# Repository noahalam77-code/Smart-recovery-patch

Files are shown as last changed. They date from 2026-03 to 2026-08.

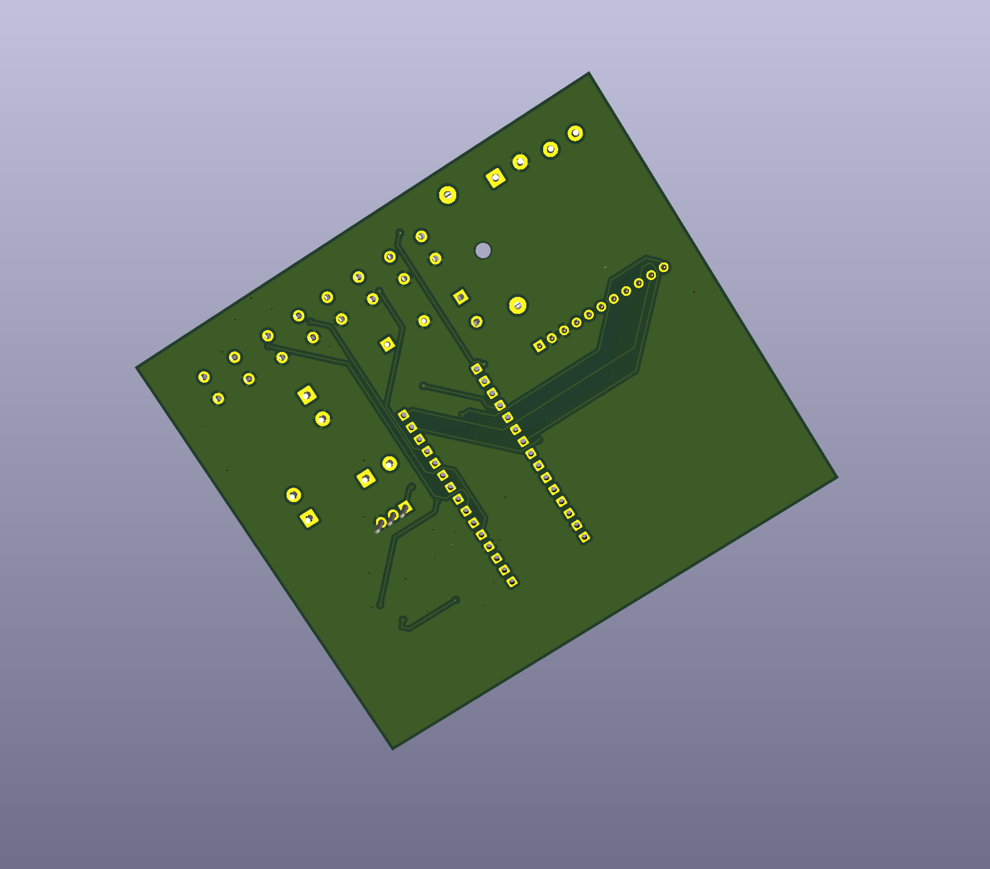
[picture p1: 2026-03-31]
pcb/Pcb3dBttm.png

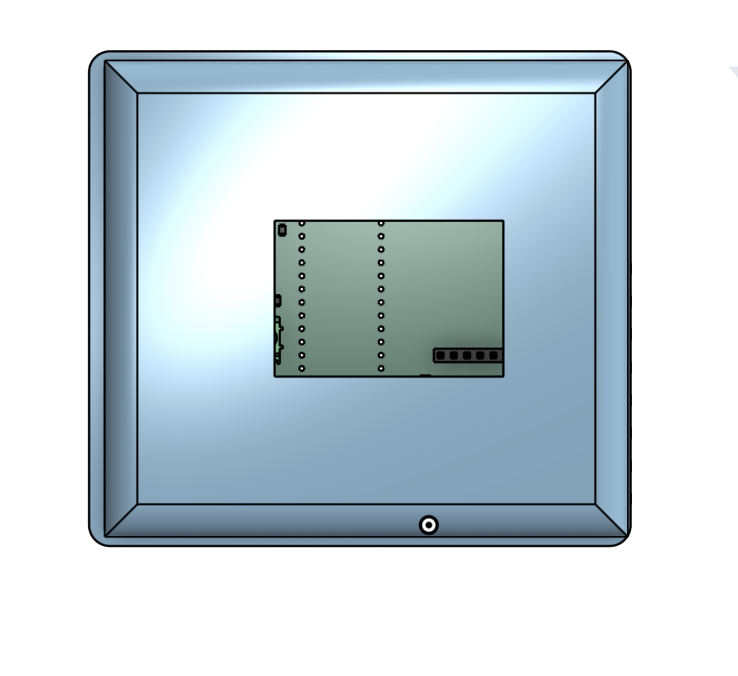
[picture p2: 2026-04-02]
CAD/CaseTop.png

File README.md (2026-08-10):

# TheraPatch

## Repository file structure
- BOM: JCLPCB BOM & regular BOM
- CADfiles: STEP files, STL files, and assembly notes
- PCB: PCB files, Gerber files, schematic images, and PCB images
- Firmware: Code & flashing instructions

## What it is
TheraPatch is a handheld therapeutic device designed to help mitigate the effects of injuries such as bruises, sprains, minor cuts, and more. By using a reverse-polarity system via an H-bridge, TheraPatch can heat the affected area (dilating blood vessels) or cool it (constricting blood vessels), both of which have been shown to help with injury healing at certain temperatures (which TheraPatch can achieve). 

## Motivation
I created TheraPatch with the primary motivation of helping people with common sports/activty related injuries while maintaining an efficient device to do so. Most of the time, when you have a bruise or scrape, you'd rely on disposable ice packs or inefficient heating pads, which are wasteful and time-consuming for long-term use. TheraPatch offers an effective, infinitely reusable solution to this. Instead of freezing water for 3-4 hours or boiling a heatpack everytime you need to reuse it, all you do with TheraPatch is plug and play. It's effective for athletes and normal people.

## Use of TheraPatch
To use the TheraPatch, first ensure your battery/wall adapter is plugged in. Then locate the 4 buttons on the top of the device; these buttons will allow you to set your desired parameters by moving through the menus: mode (hot/cold), set temp, and set time. After your desired settings are set, click the start button to initiate your therapy session, and place the side with the Peltier facing out against the affected area

## How it works
The TheraPatch looks like a simple black-and-white hot-cold block, but its guts are far more advanced. In electronics, generating heat is relatively simple. Electrons bump into each other rapidly in the wire, vibrating and thus creating the heat we feel. This is the easy part; cooling is the real engineering challenge. To cool it, I used a Peltier module, which transfers heat from one side to the other. Now, this needs to be driven by a heatsink and a fan to effectively cool. To achieve heating and cooling on the same side, I used an H bridge. The H-bridge module reverses the polarity in a Peltier module, meaning that when one side is positive and the other is negative, it cools; vice versa. All of this is controlled by a custom 4-layer PCB I designed in KiCad, with an ATmega328P as my microcontroller. The firmware reads a thermistor pressed against the Peltier plate and uses a bang-bang controller to turn the Peltier on/off to reach the desired temperature. This is all run by a rechargeable 12V battery, which charges via USB-C or a 12V wall adapter. These components are combined in a logical order in a CAD-designed box with a hole for all the input plugs and vent fans for air circulation.

Here are images of my project

## CAD imgaes:

Screenshot 2026-08-10 at 1 19 23 PM

Screenshot 2026-08-10 at 1 16 25 PM

Screenshot 2026-08-10 at 1 16 42 PM

Screenshot 2026-08-10 at 1 17 00 PM

Screenshot 2026-08-10 at 1 17 14 PM

Screenshot 2026-08-10 at 1 17 29 PM

Screenshot 2026-08-10 at 1 17 42 PM

Screenshot 2026-08-10 at 1 17 55 PM

## Link to Onshape case:

https://cad.onshape.com/documents/d627d659f05dae60588ec801/w/ad74ef98cd2d7a13cb59f9ec/e/f50ed022a94792dc2cfe6130?renderMode=0&uiState=6a4947abb17d022f5d41873a

# PCB (Signal Layer and ground):

## F.cu (signal traces and ground):

Screenshot 2026-06-03 at 1 51 27 AM

## In1.cu(ground):

Screenshot 2026-06-03 at 1 52 55 AM

## In2.cu (5V & 12V power)

Screenshot 2026-06-03 at 1 53 45 AM

## B.cu (signal traces and ground):

Screenshot 2026-06-03 at 1 54 23 AM

## 3D:

Screenshot 2026-06-03 at 1 55 00 AM

# Schematic (wiring diagram):

## Pic_1:

Screenshot 2026-06-03 at 1 55 57 AM

## Pwr:

Screenshot 2026-06-03 at 1 56 46 AM

## BOM(main)

| Item | Quantity | Unit price | Total price | Descrption | Link |
|------|----------|-----------|-------------|------------|------|
| Fan | 1 | 4.81 | 4.81 | Facliate heaitng & cooling | [Link](https://www.aliexpress.us/item/3256808462428286.html?spm=a2g0o.productlist.main.1.6babkeHNkeHNko&algo_pvid=c39052da-f6dd-4b67-816a-d90e786c586d&algo_exp_id=c39052da-f6dd-4b67-816a-d90e786c586d-0&pdp_ext_f=%7B%22order%22%3A%2262%22%2C%22eval%22%3A%221%22%2C%22fromPage%22%3A%22search%22%7D&pdp_npi=6%40dis%21USD%2111.50%214.79%21%21%2178.10%2132.53%21%402101d6ff17774285328603962e8757%2112000046088904920%21sea%21US%210%21ABX%211%210%21n_tag%3A-29910%3Bd%3Ad6b644bf%3Bm03_new_user%3A-29895%3BpisId%3A5000000204886261&curPageLogUid=VweLjIS1lGkI&utparam-url=scene%3Asearch%7Cquery_from%3A%7Cx_object_id%3A1005008648743038%7C_p_origin_prod%3A) |
| Peltier | 1 | 3.90$ | $3.90 | Cool and heat | [Link](https://www.aliexpress.us/item/3256806863842277.html?src=google&gatewayAdapt=glo2usa) |
| Heatsink | 2 | 4.80$ | $9.79 | Disspate heat | [Link](https://www.amazon.com/Awxlumv-Aluminum-60mmx60mmx15mm-Conductive-Amplifier/dp/B0DNLXD4NL) |
| LCD screen | 1 | 0.9900$ | 0.9900$ | Displaying modes | [Link](https://www.aliexpress.us/item/3256807264700302.html?spm=a2g0o.productlist.main.15.3bb1HGrhHGrhWv&algo_pvid=f071bd73-714c-4717-acaa-3f74ef8deb17&algo_exp_id=f071bd73-714c-4717-acaa-3f74ef8deb17-14&pdp_ext_f=%7B%22order%22%3A%223710%22%2C%22eval%22%3A%221%22%2C%22fromPage%22%3A%22search%22%7D&pdp_npi=6%40dis%21USD%213.14%210.99%21%21%213.14%210.99%21%4021030a6217776832914577048eb84d%2112000040806152744%21sea%21US%210%21ABX%211%210%21n_tag%3A-29910%3Bd%3Ad6b644bf%3Bm03_new_user%3A-29895%3BpisId%3A5000000203537378&curPageLogUid=GNgXD2HWAIP5&utparam-url=scene%3Asearch%7Cquery_from%3A%7Cx_object_id%3A1005007451015054%7C_p_origin_prod%3A#nav-specification) |
| Thermistor | 1 | 0.9500$ | 0.9500$ | Temp meauring | [Link](https://www.adafruit.com/product/4890?srsltid=AfmBOopGi_4mLQSeRw3V9sBgnchAdNrL2zdLeJHItTaAc1rCL6Ne9o2P) |
| Battery | 1 | 26.99$ | $26.99 | Used as main source of power (for moblity) BMS confirmed | [Link](https://liionwholesale.com/products/3s1p-3-7v-3500mah-18650-battery-with-wires-and-connector-lg-mj1-cell-inside?srsltid=AfmBOopbHVjk3o8ywzVI_wQWHKZhMZp1uCq0ynXZWNxGTDKPMvd9ZKI6&variant=31229057794117) |
| Wire | 1 | 2.2300$ | 2.23$ | Battery caddy, peliter and fan extesion | [Link](https://www.aliexpress.us/item/3256802140205012.html?spm=a2g0o.productlist.main.8.4437dfNPdfNPLw&aem_p4p_detail=202606281750527933413825797320002756170&algo_pvid=c53e4217-68c6-4b26-9b29-3624128716f9&algo_exp_id=c53e4217-68c6-4b26-9b29-3624128716f9-7&pdp_ext_f=%7B%22order%22%3A%22123%22%2C%22eval%22%3A%221%22%2C%22fromPage%22%3A%22search%22%7D&pdp_npi=6%40dis%21USD%214.70%212.79%21%21%214.70%212.79%21%402103212b17826942522901169e02c1%2112000052586672765%21sea%21US%210%21ABX%211%210%21n_tag%3A-29910%3Bd%3Ad6b644bf%3Bm03_new_user%3A-29895%3BpisId%3A5000000208023469&curPageLogUid=CY0b8Pvel5HR&utparam-url=scene%3Asearch%7Cquery_from%3A%7Cx_object_id%3A1005002326519764%7C_p_origin_prod%3A&search_p4p_id=202606281750527933413825797320002756170_2) |
| Wall adapter | 1 | $1.28 | $1.28 | 2nd way of recving power (1st battery) | [Link](https://www.aliexpress.us/item/3256806555593510.html?spm=a2g0o.productlist.main.5.103eNCpVNCpVMj&algo_pvid=3d352d1e-bc43-4e77-9d29-16e4344ed46b&algo_exp_id=3d352d1e-bc43-4e77-9d29-16e4344ed46b-4&pdp_ext_f=%7B%22order%22%3A%221992%22%2C%22eval%22%3A%221%22%2C%22fromPage%22%3A%22search%22%7D&pdp_npi=6%40dis%21USD%2111.78%211.28%21%21%2179.73%218.69%21%402101eecd17826947715547891e5012%2112000038157481542%21sea%21US%210%21ABX%211%210%21n_tag%3A-29910%3Bd%3Ad6b644bf%3Bm03_new_user%3A-29895%3BpisId%3A5000000209510139&curPageLogUid=H50idJ0yOZub&utparam-url=scene%3Asearch%7Cquery_from%3A%7Cx_object_id%3A1005006741908262%7C_p_origin_prod%3A) |
| M2 screw 8mm | 100 | 0.0100$ | $1.35 | screws for battery caddy | [Link](https://www.aliexpress.us/item/2251832857570651.html?spm=a2g0o.productlist.main.3.4e3cdUVEdUVEfl&algo_pvid=ea8d64ad-4af7-4109-af97-4e674e97f9e5&algo_exp_id=ea8d64ad-4af7-4109-af97-4e674e97f9e5-2&pdp_ext_f=%7B%22order%22%3A%2216288%22%2C%22eval%22%3A%221%22%2C%22fromPage%22%3A%22search%22%7D&pdp_npi=6%40dis%21USD%211.35%210.99%21%21%211.35%210.99%21%402103129f17825915196483426e5a8e%2112000020018123413%21sea%21US%210%21ABX%211%210%21n_tag%3A-29910%3Bd%3Ad6b644bf%3Bm03_new_user%3A-29895%3BpisId%3A5000000208023469&curPageLogUid=WMcjfyJWRpdQ&utparam-url=scene%3Asearch%7Cquery_from%3A%7Cx_object_id%3A33043885403%7C_p_origin_prod%3A) |
| M2 screw 14mm | 100 | 0.0100$ | $1.35 | screws for main case | [Link](https://www.aliexpress.us/item/2251832857570651.html?spm=a2g0o.productlist.main.3.4e3cdUVEdUVEfl&algo_pvid=ea8d64ad-4af7-4109-af97-4e674e97f9e5&algo_exp_id=ea8d64ad-4af7-4109-af97-4e674e97f9e5-2&pdp_ext_f=%7B%22order%22%3A%2216288%22%2C%22eval%22%3A%221%22%2C%22fromPage%22%3A%22search%22%7D&pdp_npi=6%40dis%21USD%211.35%210.99%21%21%211.35%210.99%21%402103129f17825915196483426e5a8e%2112000020018123413%21sea%21US%210%21ABX%211%210%21n_tag%3A-29910%3Bd%3Ad6b644bf%3Bm03_new_user%3A-29895%3BpisId%3A5000000208023469&curPageLogUid=WMcjfyJWRpdQ&utparam-url=scene%3Asearch%7Cquery_from%3A%7Cx_object_id%3A33043885403%7C_p_origin_prod%3A) |
| Dupont connectors | 40 | 0.0253$ | 1.01$ | connectors for LCD and ISP proggarmer | [Link](https://www.aliexpress.us/item/3256809185840584.html?spm=a2g0o.productlist.main.4.7725T11aT11aC1&aem_p4p_detail=202606272107031134387990076280002008158&algo_pvid=84f900fb-1f7e-4029-80e1-2e2e9eab2415&algo_exp_id=84f900fb-1f7e-4029-80e1-2e2e9eab2415-3&pdp_ext_f=%7B%22order%22%3A%22686%22%2C%22eval%22%3A%221%22%2C%22fromPage%22%3A%22search%22%7D&pdp_npi=6%40dis%21USD%211.56%211.01%21%21%2110.57%216.87%21%402101e80317826196231237198ed5a5%2112000048899602396%21sea%21US%210%21ABX%211%210%21n_tag%3A-29910%3Bd%3Ad6b644bf%3Bm03_new_user%3A-29895%3BpisId%3A5000000208023469&curPageLogUid=48BAjk6LrSZa&utparam-url=scene%3Asearch%7Cquery_from%3A%7Cx_object_id%3A1005009372155336%7C_p_origin_prod%3A&search_p4p_id=202606272107031134387990076280002008158_2) |
| ISP porgrammer | 1 | 1.9100$ | $1.91 | Flashes code onto the ATMega chip | [Link](https://www.aliexpress.us/item/3256810618247711.html?spm=a2g0o.productlist.main.2.71a9WonxWonxOW&algo_pvid=013dc172-5dcd-4517-a7dc-e44b31c61f77&algo_exp_id=013dc172-5dcd-4517-a7dc-e44b31c61f77-1&pdp_ext_f=%7B%22order%22%3A%2220%22%2C%22eval%22%3A%221%22%2C%22fromPage%22%3A%22search%22%7D&pdp_npi=6%40dis%21USD%212.41%211.91%21%21%212.41%211.91%21%402101d6ff17826055513113304ea732%2112000053555380165%21sea%21US%210%21ABX%211%210%21n_tag%3A-29910%3Bd%3Ad6b644bf%3Bm03_new_user%3A-29895%3BpisId%3A5000000208023469&curPageLogUid=atD9pSQGrkCO&utparam-url=scene%3Asearch%7Cquery_from%3A%7Cx_object_id%3A1005010804562463%7C_p_origin_prod%3A) |
| Buttons | 20 | 0.1095$ | 2.19$ | Switching between menus & 0start/stop | [Link](https://www.aliexpress.us/item/3256801638385730.html?spm=a2g0o.productlist.main.18.6eae9KoY9KoY39&algo_pvid=a04722e0-ab76-4104-b323-04a47393d95b&algo_exp_id=a04722e0-ab76-4104-b323-04a47393d95b-17&pdp_ext_f=%7B%22order%22%3A%2239%22%2C%22eval%22%3A%221%22%2C%22fromPage%22%3A%22search%22%7D&pdp_npi=6%40dis%21USD%213.15%212.59%21%21%213.15%212.59%21%402101eee917825893617621165ec559%2112000017947649837%21sea%21US%210%21ABX%211%210%21n_tag%3A-29910%3Bd%3Ad6b644bf%3Bm03_new_user%3A-29895%3BpisId%3A5000000208023469&curPageLogUid=ypVEuRkxBtEG&utparam-url=scene%3Asearch%7Cquery_from%3A%7Cx_object_id%3A1005001824700482%7C_p_origin_prod%3A) |
| Terminal Block | 5 | 0.0864$ | 0.4300$ | For conencting things without JST conenctor | [Link](https://www.lcsc.com/product-detail/C394556.html?s_z=n_JILN%2520JL126-50002G01) |
| Barrel Jack | 5 | 0.1462$ | $0.73 | Wall power input | [Link](https://www.lcsc.com/product-detail/C720558.html?s_z=n_q_barrel%2520jack%25205A&spm=wm.fly.bg.0.xh&lcsc_vid=QFJaAQFeTlFdU1xXTwILAlBQQQILVwYAQQALAlYEFFYxVlNRTlVfU1NRRlVfXzsOAxUeFF5JWBYZEEoKFBINSQcJGk4NBhADEA4cHktRRVBADxALGw%3D%3D) |
| JST female | 20 | 0.0403$ | 0.81$ | Battery inpt | [Link](https://www.lcsc.com/product-detail/C158012.html?s_z=n_q_C158012&globalKeyword=C158012) |
| 4 Pin connector for LCD | 10 | 0.0807$ | 0.81$ | LCD input | [Link](https://www.lcsc.com/product-detail/C50950.html?s_z=n_q_C50950&globalKeyword=C50950) |
| Arundio flash input | 5 | 0.2238$ | 1.12$ | Pins to flash code | [Link](https://www.lcsc.com/product-detail/C50980.html?s_z=n_q_C50980&globalKeyword=C50980) |
| USB-C | 5 | $0.1857 | $0.93 | Charging | [Link](https://www.lcsc.com/product-detail/C165948.html?s_z=n_q_C165948&globalKeyword=C165948) |
| 5A fuse | 10 | 0.0506$ | $0.51 | PCB | [Link](https://www.lcsc.com/product-detail/C41367229.html?s_z=n_q_t_5A%2520smd%2520fuse&spm=wm.fly.bg.0.xh___wm.ssy.tc.1.tz&lcsc_vid=QFJaAQFeTlFdU1xXTwILAlBQQQILVwYAQQALAlYEFFYxVlNRX1JWRFhbVTsOAxUeFF5JWBYZEEoKFBINSQcJGk4eFQsCAgIaSgADAwAHC0slQ1hcUV1ST1ZADxALGw%3D%3D) |
| 16 Mhz cyrstal | 5 | 0.2372$ | $1.19 | PCB | [Link](https://www.lcsc.com/product-detail/C122519.html?s_z=n_q_C122519&globalKeyword=C122519) |
| Ferrite Bead | 10 | 0.0262$ | $0.26 | PCB | [Link](https://www.lcsc.com/product-detail/C21519.html?s_z=n_q_600%2520ohm%2520ferrite%2520bead%25200805&spm=wm.fly.bg.0.xh&lcsc_vid=QFJaAQFeTlFdU1xXTwILAlBQQQILVwYAQQALAlYEFFYxVlNRTlNeUFZWRFZaXjsOAxUeFF5JWBYZEEoKFBINSQcJGk4eFQsCAgIaSgADAwAHC0slQFFbUVZIHxUDCw%3D%3D) |
| AO3400A | 5 | 0.0846$ | $0.42 | diode for the fan | [Link](https://www.lcsc.com/product-detail/C20917.html?s_z=n_q_C20917&globalKeyword=C20917) |
| SS54 Diode | 10 | 0.0366$ | 0.3700$ | Diode used in buck and input pwr | [Link](https://www.lcsc.com/product-detail/C22452.html?s_z=n_q_SS54%2520diode&spm=wm.fly.bg.0.xh&lcsc_vid=QFJaAQFeTlFdU1xXTwILAlBQQQILVwYAQQALAlYEFFYxVlNRTlNaVVRURldfUzsOAxUeFF5JWBYZEEoKFBINSQcJGk4eFQsCAgIaSgADAwAHC0slT1dZUUoOAwwC) |
| 33uH buck Inductor | 5 | 0.2204$ | 1.10$ | PCB | [Link](https://www.lcsc.com/product-detail/C9400.html?s_z=n_q_t_33uH%2520SMD%2520ind&spm=wm.fly.bg.0.xh___wm.ssy.tc.0.tz&lcsc_vid=QFJaAQFeTlFdU1xXTwILAlBQQQILVwYAQQALAlYEFFYxVlNRT1leX1JUQFNXUTsOAxUeFF5JWBYZEEoKFBINSQcJGk4dAgUUFAk%3D) |
| 2.2uH boost Inductor | 5 | 0.1161$ | $0.58 | PCB | [Link](https://www.lcsc.com/product-detail/C7461347.html?s_z=n_q_CXP0530-2R2M-AG&spm=wm.fly.bg.0.xh&lcsc_vid=QFJaAQFeTlFdU1xXTwILAlBQQQILVwYAQQALAlYEFFYxVlNRT1leX11TRlhaUjsOAxUeFF5JWBYZEEoKFBINSQcJGk4NBhADEA4cHktXRllfSQwSGg0%3D) |
| 120K resistor | 100 | $0.0022 | $0.22 | PCB | [Link](https://www.lcsc.com/product-detail/C2907223.html?s_z=n_q_C2907223&globalKeyword=C2907223) |
| 90K resitor | 10 | $0.0654 | $0.65 | PCB | [Link](https://www.lcsc.com/product-detail/C5123603.html?s_z=n_q_C5123603&globalKeyword=C5123603) |
| 68K resistor | 100 | $0.0021 | $0.21 | PCB | [Link](https://www.lcsc.com/product-detail/C2907283.html?s_z=n_q_C2907283&globalKeyword=C2907283) |
| 51k resistor | 100 | $0.0021 | $0.21 | PCB | [Link](https://www.lcsc.com/product-detail/C2933461.html?s_z=n_q_C2933461&globalKeyword=C2933461) |
| 47K resistor | 100 | $0.0021 | $0.21 | PCB | [Link](https://www.lcsc.com/product-detail/C2930202.html?s_z=n_q_C2930202&globalKeyword=C2930202) |
| 10K resistor | 100 | $0.0020 | $0.20 | PCB | [Link](https://www.lcsc.com/product-detail/C2907219.html?s_z=n_q_C2907219&globalKeyword=C2907219) |
| 5.1K resistor | 100 | $0.00 | $0.27 | PCB | [Link](https://www.lcsc.com/product-detail/C27834.html?s_z=n_q_C27834&globalKeyword=C27834) |
| 3.3K resistor | 100 | $0.0020 | $0.20 | PCB | [Link](https://www.lcsc.com/product-detail/C2907023.html?s_z=n_q_t_3.3K%2520resistor&spm=wm.fly.bg.1.xh___wm.ssy.tc.0.tz&lcsc_vid=QFJaAQFeTlFdU1xXTwILAlBQQQILVwYAQQALAlYEFFYxVlNRT1lfUVBUTlNfXzsOAxUeFF5JWBYZEEoKFBINSQcJGk4eFQsCAgIaSgADAwAHC0slRVZWVFBIHxUDCw%3D%3D) |
| 1k resistor | 100 | $0.0076 | $0.76 | PCB | [Link](https://www.lcsc.com/product-detail/C2907002.html?s_z=n_q_t_0603%25201k%25CE%25A9%2520&spm=wm.fly.bg.0.xh___wm.ssy.tc.0.tz&lcsc_vid=QFJaAQFeTlFdU1xXTwILAlBQQQILVwYAQQALAlYEFFYxVlNeRFBXUFRQT1NcUzsOAxUeFF5JWBYZEEoKFBINSQcJGk4NBhADEA4cHktXRlhXSQwSGg0%3D) |
| 100Ω resistor | 100 | $0.0014 | $0.14 | PCB | [Link](https://www.lcsc.com/product-detail/C105588.html?s_z=n_q_t_100%25CE%25A9%2520resistor&spm=wm.fly.bg.0.xh___wm.ssy.tc.0.tz&lcsc_vid=QFJaAQFeTlFdU1xXTwILAlBQQQILVwYAQQALAlYEFFYxVlNRT1lfUVxWQ1RbXzsOAxUeFF5JWBYZEEoKFBINSQcJGk4NBhADEA4cHktXRlhXSQwSGg0%3D) |
| 470uF capacitor | 5 | $0.0875 | $0.44 | PCB | [Link](https://www.lcsc.com/product-detail/C976030.html) |
| 220uF capacitor | 10 | $0.0276 | $0.28 | PCB | [Link](https://www.lcsc.com/product-detail/C22388075.html?s_z=n_q_220uF%2520%25C2%25B120%2525%252025V%2520Aluminum%2520Electrolytic%2520Capacitors%2520SMD&spm=wm.fly.bg.0.xh&lcsc_vid=QFJaAQFeTlFdU1xXTwILAlBQQQILVwYAQQALAlYEFFYxVlNRT1lfUFxUQ1NdVjsOAxUeFF5JWBYZEEoKFBINSQcJGk4NBhADEA4cHktXRlVeSQwSGg0%3D) |
| 100uF capacitor | 20 | $0.0372 | $0.74 | PCB | [Link](https://www.lcsc.com/product-detail/C970685.html?s_z=n_q_C970685&globalKeyword=C970685) |
| 22uF capacitor | 20 | $0.0349 | $0.70 | PCB | [Link](https://www.lcsc.com/product-detail/C45783.html?s_z=n_q_C45783&globalKeyword=C45783) |
| 10uF capacitor | 10 | $0.0394 | $0.39 | PCB | [Link](https://www.lcsc.com/product-detail/C9807.html?s_z=n_q_10uF%2520%25C2%25B110%2525%252025V%2520Ceramic%2520Capacitor&spm=wm.fly.bg.0.xh&lcsc_vid=QFJaAQFeTlFdU1xXTwILAlBQQQILVwYAQQALAlYEFFYxVlNRT1lfUFNSQVNXVDsOAxUeFF5JWBYZEEoKFBINSQcJGk4eFQsCAgIaSgADAwAHC0slRlRWUlRIHxUDCw%3D%3D) |
| 1uF capacitor | 50 | $0.0069 | $0.35 | PCB | [Link](https://www.lcsc.com/product-detail/C29936.html?s_z=n_q_1uF%2520%25C2%25B110%2525%252025V%2520Ceramic%2520Capacitor%2520&spm=wm.fly.bg.0.xh&lcsc_vid=QFJaAQFeTlFdU1xXTwILAlBQQQILVwYAQQALAlYEFFYxVlNRT1lfUFBfTlhZUTsOAxUeFF5JWBYZEEoKFBINSQcJGk4eFQsCAgIaSgADAwAHC0slQlBXXlxRRU8GEwkK) |
| 0.1uF capacitor | 100 | $0.004 | $0.40 | PCB | [Link](https://www.lcsc.com/product-detail/C1590.html?s_z=n_q_100nF%2520%25C2%25B110%2525%252025V%2520Ceramic%2520Capacitor%2520&spm=wm.fly.bg.0.xh&lcsc_vid=QFJaAQFeTlFdU1xXTwILAlBQQQILVwYAQQALAlYEFFYxVlNRT1lfUFFfRVVdVzsOAxUeFF5JWBYZEEoKFBINSQcJGk4eFQsCAgIaSgADAwAHC0slRlVYUVdIHxUDCw%3D%3D) |
| 22pF capacitor | 100 | $0.0041 | $0.41 | PCB | [Link](https://www.lcsc.com/product-detail/C1653.html?s_z=n_q_C1653&globalKeyword=C1653) |
| ST VNH5019ATR-E | 1 | 9.36$ | 9.36$ | H-bridge to switch polairty | [Link](https://www.lcsc.com/product-detail/C2653552.html?s_z=n_VNH5019A-E&spm=wm.ssy.bg.0.stp&lcsc_vid=QFJaAQFeTlFdU1xXTwILAlBQQQILVwYAQQALAlYEFFYxVlNRQ1VZV1NQRFZcUjsOAxUeFF5JWBYZEEoKFBINSQcJGk4eFQsCAgIaSgADAwAHC0slQlJZUlRIHxUDCw%3D%3D) |
| LM2596S-5.0 | 1 | 1.42$ | 1.37$ | Buck convetor for non 12V parts | [Link](https://www.lcsc.com/product-detail/C116713.html?s_z=n_LM2596S-5&spm=wm.ssy.bg.17.xh&lcsc_vid=QFJaAQFeTlFdU1xXTwILAlBQQQILVwYAQQALAlYEFFYxVlNRQ1VZVVdQR1leVjsOAxUeFF5JWBYZEEoKFBINSQcJGk4eFQsCAgIaSgADAwAHC0slRlRdVVZUWQkaCgg%3D) |
| WCH CH224K | 1 | $0.61 | $0.61 | Power negogatior, Requests 9V | [Link](https://www.lcsc.com/product-detail/C970725.html?s_z=n_q_CH224K&spm=wm.ssy.bg.0.xh&lcsc_vid=QFJaAQFeTlFdU1xXTwILAlBQQQILVwYAQQALAlYEFFYxVlNRQFZaUldfQlhfVjsOAxUeFF5JWBYZEEoKFBINSQcJGk4dAgUUFAk%3D) |
| IP2326 | 1 | $0.62 | $0.62 | Boost converter for charging 9V to 12.6V | [Link](https://www.lcsc.com/product-detail/C2832094.html?s_z=n_q_IP2326&spm=wm.fly.bg.0.xh&lcsc_vid=QFJaAQFeTlFdU1xXTwILAlBQQQILVwYAQQALAlYEFFYxVlNRT1lfVVxfQFdeXzsOAxUeFF5JWBYZEEoKFBINSQcJGk4eFQsCAgIaSgADAwAHC0slTlZeUFZTWQkaCgg%3D) |
| ATMEGA328P-AU | 1 | $2.65 | $2.65 | Microcontroller | [Link](https://www.lcsc.com/product-detail/C14877.html?s_z=n_q_ATmega328P-A&spm=wm.fly.bg.0.xh&lcsc_vid=QFJaAQFeTlFdU1xXTwILAlBQQQILVwYAQQALAlYEFFYxVlNRT1lfVFReT1FZVTsOAxUeFF5JWBYZEEoKFBINSQcJGk4eFQsCAgIaSgADAwAHC0slRVldVVRfQ08GEwkK) |

## BOM(JLCPCB)

| Comment | Designator | Footprint | LCSC Part Number |
|---------|-----------|-----------|------------------|
| USB-C | USBC1 | USBC_U:USB-C_SMD-TYPE-C-31-M-12_1 | C165948 |
| 5A Fuse | F2 | Fuse:Fuse_1206_3216Metric | C41367229 |
| Crystal | Y1 | Crystal:Crystal_SMD_5032-2Pin_5.0x3.2mm | C122519 |
| Ferrite bead | FB1 | Inductor_SMD:L_0805_2012Metric | C21519 |
| AO3400A diode | Q4 | Package_TO_SOT_SMD:SOT-23 | C20917 |
| SS54 Diode | D1, D2, D3, D6 | Diode_SMD:D_SMA | C22452 |
| 33µH inductor | L1 | inductor_33uh:IND-SMD_L12.3-W12.3 | C9400 |
| 120K Resitor | R21, R35 | Resistor_SMD:R_0805_2012Metric | C2907223 |
| 90K Resitor | R24 | Resistor_SMD:R_0805_2012Metric | C5123603 |
| 68K Resitor | R22 | Resistor_SMD:R_0805_2012Metric | C2907283 |
| 51K Resitor | R20 | Resistor_SMD:R_0805_2012Metric | C2933461 |
| 47K restior | R27 | Resistor_SMD:R_0805_2012Metric | C2930202 |
| 10K Restior | R34, R33, R28, R16, R13, R12, R10, R9, R8, R5, R3, R2, R1 | Resistor_SMD:R_0805_2012Metric | C2907219 |
| 5.1K resistor | R18, R19 | Resistor_SMD:R_0805_2012Metric | C27834 |
| 3.3K resistor | R7, R14 | Resistor_SMD:R_0603_1608Metric | C2907023 |
| 1k resistor | R32, R23, R17, R15, R6, R4 | Resistor_SMD:R_0603_1608Metric | C2907002 |
| 100Ω resistor | R11 | Resistor_SMD:R_0603_1608Metric | C105588 |
| 220uF capacitor | C2 | Capacitor_SMD:CP_Elec_6.3x7.7 | C22388075 |
| 100uF capacitor | C8 | Capacitor_SMD:CP_Elec_6.3x7.7 | C970685 |
| 22uF capacitor | C14, C17 | Capacitor_SMD:C_0805_2012Metric | C45783 |
| 10uF capacitor | C25, C23, C22,C10 | Capacitor_SMD:C_1206_3216Metric | C9807 |
| 1uF capacitor | C7 | Capacitor_SMD:C_0603_1608Metric | C29936 |
| 0.1uF capacitor | C24, C19, C18, C15, C13, C12, C11, C9, C6, C5, C4, C3, C1 | Capacitor_SMD:C_0603_1608Metric | C1590 |
| 22pF capacitor | C20,C21 | Capacitor_SMD:C_0603_1608Metric | C1653 |
| ST VNH5019ATR-E | U2 | Package_SO:ST_MultiPowerSO-30 | C2653552 |
| LM2596S-5.0 | U1 | Package_TO_SOT_SMD:TO-263-5_TabPin3 | C116713 |
| WCH CH224K | U3 | CH224K:ESSOP-10_L4.9-W3.9-P1.0-LS6.0-TL-EP | C970725 |
| IP2326 | U5 | Package_DFN_QFN:QFN-24-1EP_4x4mm_P0.5mm_EP2.6x2.6mm | C2832094 |
| ATMEGA328P-AU | U4 | Package_QFP:TQFP-32_7x7mm_P0.8mm | C14877 |

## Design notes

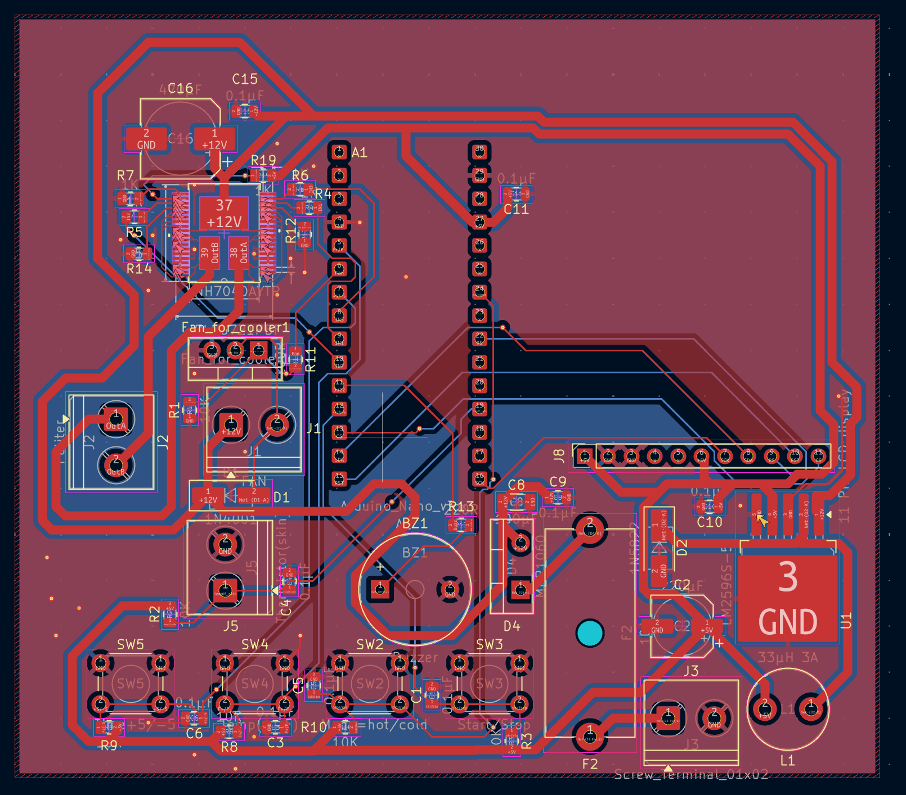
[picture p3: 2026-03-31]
pcb/pcb.png

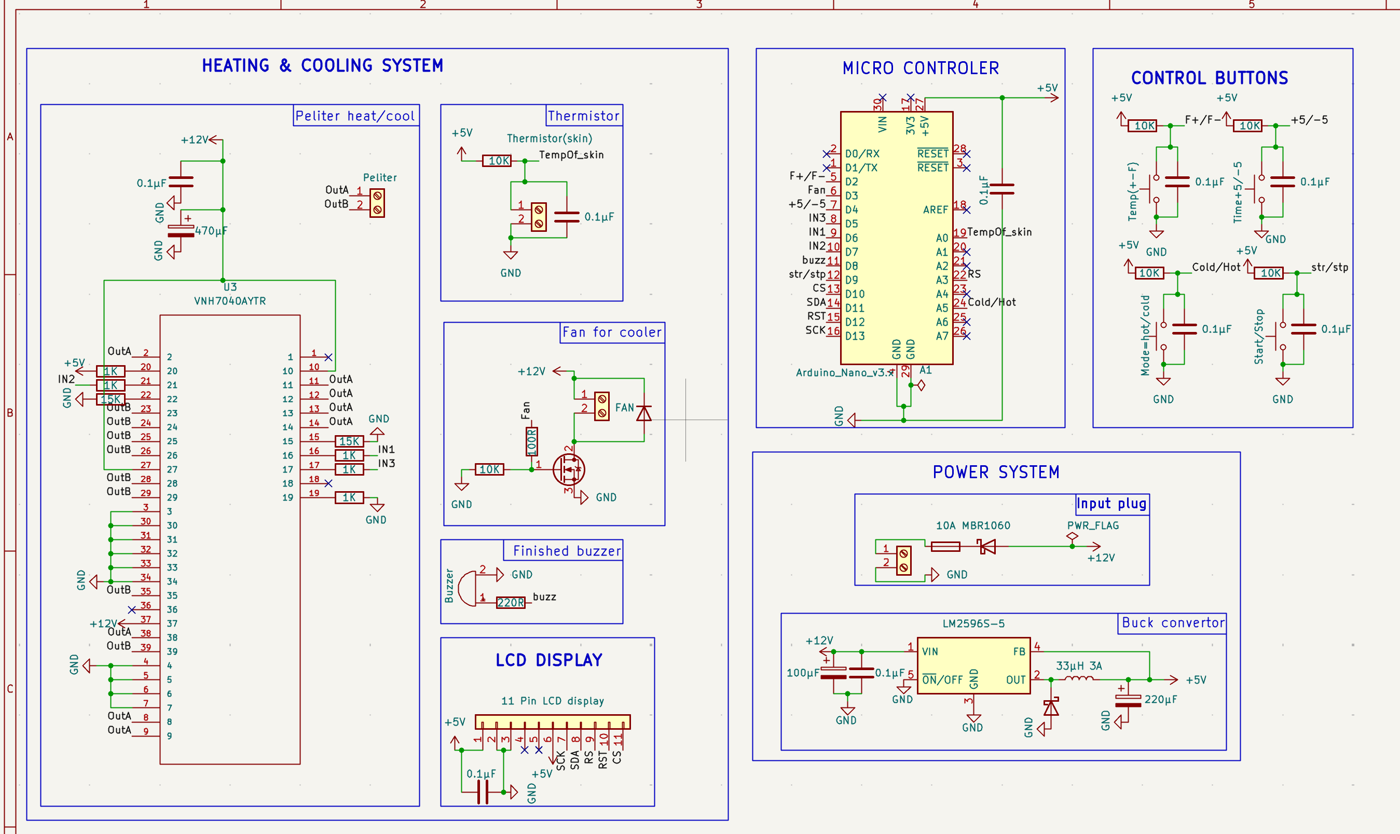
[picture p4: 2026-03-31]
pcb/Sch.png

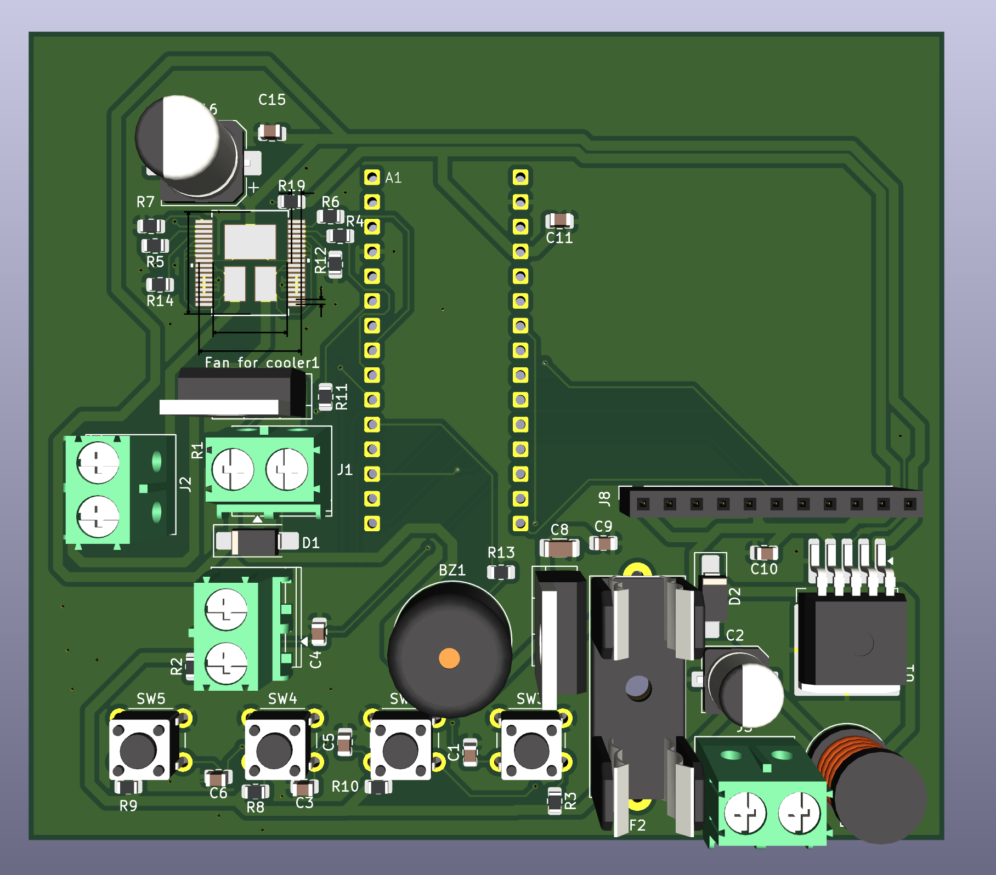
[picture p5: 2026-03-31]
pcb/Pcb3dTop.png

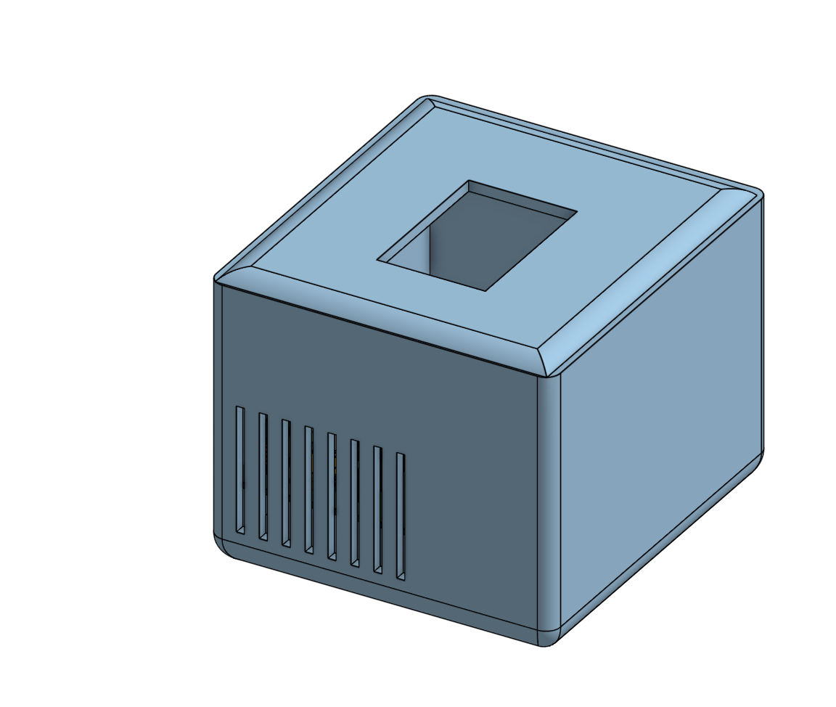
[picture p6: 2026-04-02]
CAD/CASE.png

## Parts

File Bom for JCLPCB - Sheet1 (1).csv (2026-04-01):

Comment | Designator | Footprint | LCSC Part Number
VNH7040AYTR | U3 | VNH7040AYTR:POWERSSO-36TP_STM | C2969764
LM2596S-5.0/NOPB | U1 | Package_TO_SOT_SMD:TO-263-5_TabPin3 | C116713
1N4001 | D1 | Diode_SMD:D_SMA_Handsoldering | C2909965
1N5822 | D2 | Diode_SMD:D_SMA_Handsoldering | C8678
15K | R12, R14 | Resistor_SMD:R_0805_2012Metric | C17475
10K | R1, R2, R3, R8, R9, R10 | Resistor_SMD:R_0805_2012Metric | C84376
1K | R4, R5, R6, R7, R19 | Resistor_SMD:R_0805_2012Metric | C95781
220R | R13 | Resistor_SMD:R_0805_2012Metric | C17557
100R | R11 | Resistor_SMD:R_0805_2012Metric | C17408
0.1µF | C1, C3, C4, C5, C6, C9, C10, C11, C15 | Capacitor_SMD:C_0805_2012Metric | C49678
100 µF | C8 | Capacitor_SMD:C_1206_3216Metric | C15008
220 µF | C2 | Capacitor_SMD:CP_Elec_6.3x7.7 | C4747974
470 µF | C16 | Capacitor_SMD:CP_Elec_8x10.5 | C48935394

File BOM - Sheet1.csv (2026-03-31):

Item | Quantity | Unit price | Total price | Link
Arduino Nano V3.0 | 1 | 0.9900$ | 0.9900$ | https://www.aliexpress.us/item/3256806880365712.html
Peltier Heat&cool | 1 | 8.9900$ | 8.9900$ | https://www.amazon.com/gp/product/B0CBDNS9H6/ref=ox_sc_act_image_5?smid=A1YZW40LYQY3L1&psc=1
LCD screen | 1 | 8.9500$ | 8.9500$ | https://www.amazon.com/gp/product/B0FB8NK5X9/ref=ox_sc_act_image_4?smid=ACSUDGHCXWYXE&psc=1
Buzzer | 1 | 0.9200$ | 0.9200$ | https://www.lcsc.com/product-detail/C96093.html?s_z=n_buzzer%2520
ST VNH7040AYTR | 1 | 2.8334$ | 2.8334$ | https://www.lcsc.com/product-detail/C2969764.html?s_z=n_C2969764
IRLB8721PBF | 1 | 2.9100$ | 2.9100$ | https://www.lcsc.com/product-detail/C153222.html?s_z=n_IRLB8721PBF
LM2596S-5.0 | 1 | 1.4200$ | 1.4200$ | https://www.lcsc.com/product-detail/C116713.html?s_z=n_LM2596S-5
1N5822 | 20 | 0.0295$ | 0.5900$ | https://www.lcsc.com/product-detail/C8678.html
MBR1060 | 1 | 1.0500$ | 1.0500$ | https://www.digikey.com/en/products/detail/smc-diode-solutions/MBR1060/6022112
1N4001 | 1 | 0.0125$ | 0.0125$ | https://www.lcsc.com/product-detail/C2909965.html?s_z=n_1N4001%2520SMA
Inductior | 5 | 0.4700$ | 2.3500$ | https://www.aliexpress.us/item/3256806685342889.html?aem_p4p_detail=2026032520020429883245200005387612&curPageLogUid=fgRSBES7zEeR
Fuse | 1 | 3.4800$ | 3.4800$ | https://www.aliexpress.us/item/3256806025997155.html?curPageLogUid=mMCqISV6gF1x
10K Resitor | 100 | 0.0023$ | 0.23 | https://www.lcsc.com/product-detail/C84376.html?s_z=n_10K%2520Resistor%25200805
1K Resit | 100 | 0.0025$ | 0.25 | https://www.lcsc.com/product-detail/C95781.html?s_z=n_RC0805FR-071KL
3.3K Resitor | 100 | 0.0020$ | 0.21 | https://www.lcsc.com/product-detail/C2907249.html?s_z=n_3.3K%2520Resistor%25200805
220 Ohm Resitor | 100 | 0.0024$ | 0.24 | https://www.lcsc.com/product-detail/C17557.html?s_z=n_220%25CE%25A9%2520Resistor%25200805
100 ohm resitor | 100 | 0.0021$ | 0.21 | https://www.lcsc.com/product-detail/C17408.html?s_z=n_100%25CE%25A9%2520Resistor%25200805
0.1µF Captior | 100 | 0.0051$ | 0.51 | https://www.lcsc.com/product-detail/C49678.html?s_z=n_LCSC%2520C49678
220uF Capatior | 20 | 0.0339$ | 0.68 | https://www.lcsc.com/product-detail/C4747974.html?s_z=n_220uF%252025V%2520radial%2520D8
470uF Capatior | 5 | 0.0800$ | 0.4 | https://www.lcsc.com/product-detail/C48935394.html?s_z=n_470uF%252025V%2520SMD%2520electrolytic
Termnial Block | 5 | 0.0904$ | 0.45 | https://www.lcsc.com/product-detail/C394556.html?s_z=n_JILN%2520JL126-50002G01
Female 11 pin header | 1 | 1.6100$ | 1.61 | https://www.ebay.com/itm/177501535604?chn=ps&google_free_listing_action=view_item
Buttons | 20 | 0.0495$ | 0.99 | https://www.aliexpress.us/item/3256801626723541.html?curPageLogUid=1eLJ6XUF45iq
100uF Capatior | 1 | 0.0610$ | 0.61 | https://www.lcsc.com/product-detail/C15008.html?s_z=n_Samsung%25201206%2520SMD
Themisotr | 1 | 1.2900$ | 1.29 | https://www.aliexpress.us/item/3256807948165582.html?curPageLogUid=aQ76dfXS5OT1
15k ohm resitor | 100 | 0.0023 | 0.23 | https://www.lcsc.com/product-detail/C17475.html

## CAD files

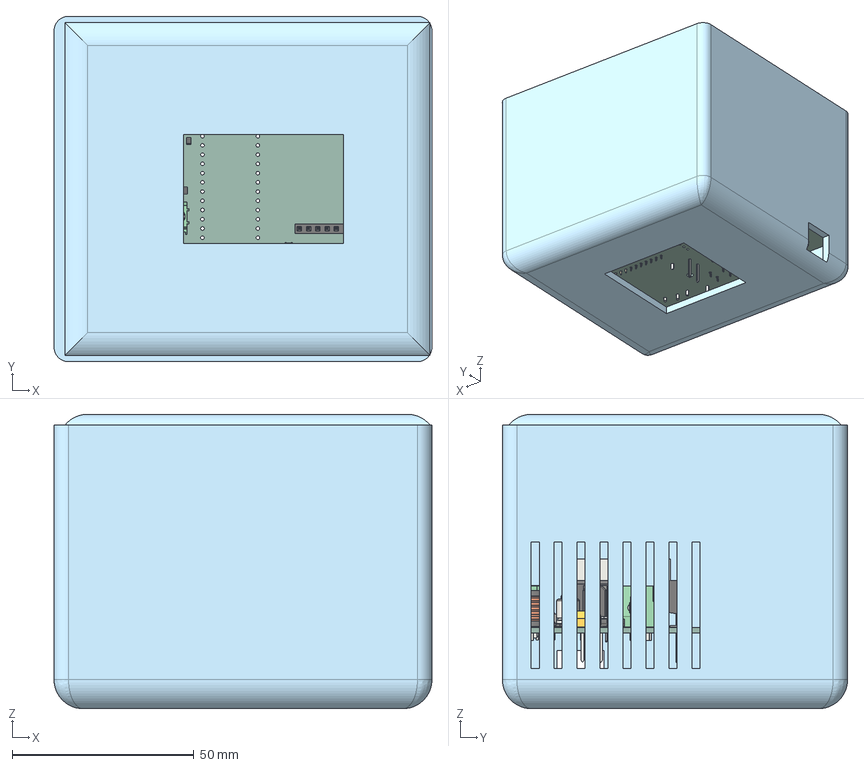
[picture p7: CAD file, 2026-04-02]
CAD/Assembly 1.step
104.0 x 95.0 x 81.0 mm
TeraPATCCH 1.3.1 x 7
D_SMA x 2
C_0805_2012Metric x 9
Fuseholder_Cylinder-5x20mm_Schurter_0031_8201_Horizontal_Open
SW_PUSH_6mm_H4.3mm x 4
R_0805_2012Metric x 15
TO-220-2_Vertical
TO-220-3_Vertical
TerminalBlock_Phoenix_PT-1,5-2-5.0-H_1x02_P5.00mm_Horizontal x 4
C_1206_3216Metric
Buzzer_12x9.5RM7.6
CP_Elec_8x10.5
CP_Elec_6.3x7.7
PinSocket_1x11_P2.54mm_Vertical
Bio_thing_PCB
L_Radial_D8.7mm_P5.00mm_Fastron_07HCP

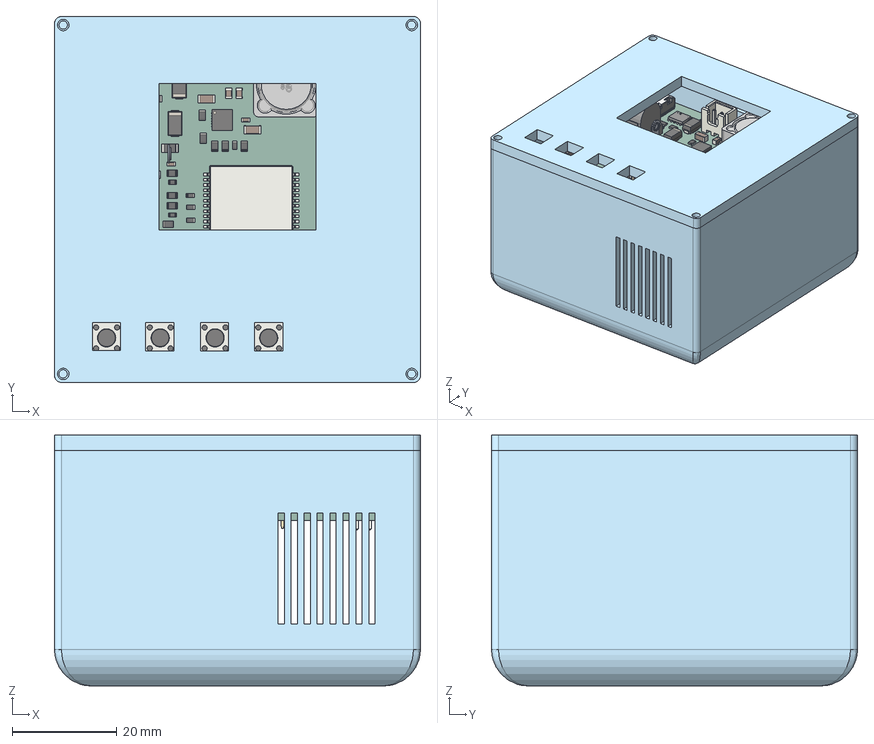
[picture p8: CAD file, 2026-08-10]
CADfiles/TheraPatch Assembly (2).step
70.0 x 70.0 x 48.0 mm
JST_XH_B2B-XH-A_1x02_P2.50mm_Vertical x 3
ESSOP-10_L4.9-W3.9-P1.0-LS6.0-TL-EP x 14
R_0805_2012Metric x 21
USB-C_SMD-TYPE-C-31-M-12_1 x 13
C_0603_1608Metric x 16
R_0603_1608Metric x 9
D_SMA x 4
SMD-PIND_L12.5-W12.5-H8.0 x 6
TQFP-32_7x7mm_P0.8mm
PinSocket_1x04_P2.54mm_Vertical
CP_Elec_6.3x7.7 x 2
C_0805_2012Metric x 2
L_0805_2012Metric
DC-IN-TH_DC-005-A250 x 3
SW_PUSH_6mm_H4.3mm x 4
C_1206_3216Metric x 4
Crystal_SMD_5032-2Pin_5.0x3.2mm
Fuse_1206_3216Metric
PinHeader_2x03_P2.54mm_Vertical
QFN-24-1EP_4x4mm_P0.5mm_EP2.6x2.6mm
ST_MultiPowerSO-30
SOT-23
CP_Elec_10x10.5
Bio_thing_PCB
Terapatach 1.77.1 x 7

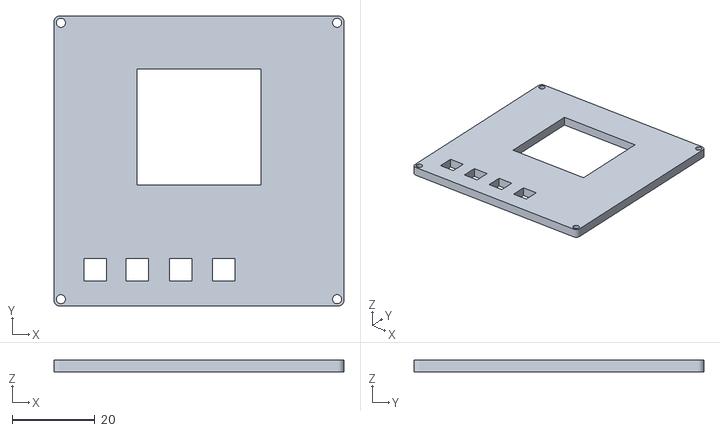
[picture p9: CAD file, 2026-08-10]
CADfiles/Lid (1).stl
70.0 x 70.0 x 3.00

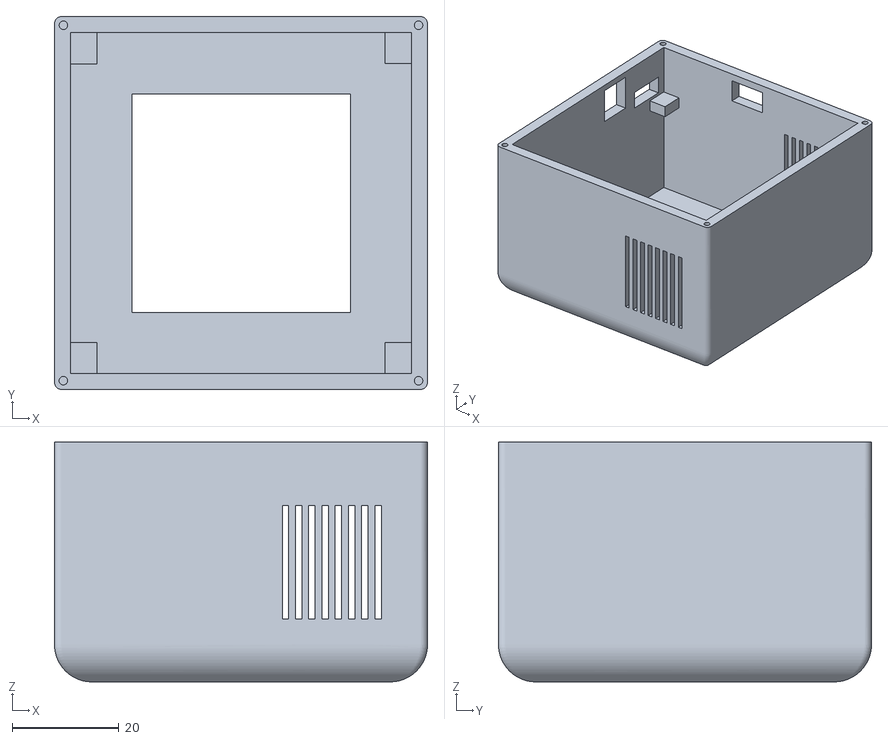
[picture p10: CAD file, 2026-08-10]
CADfiles/case (1).stl
70.0 x 70.0 x 45.0

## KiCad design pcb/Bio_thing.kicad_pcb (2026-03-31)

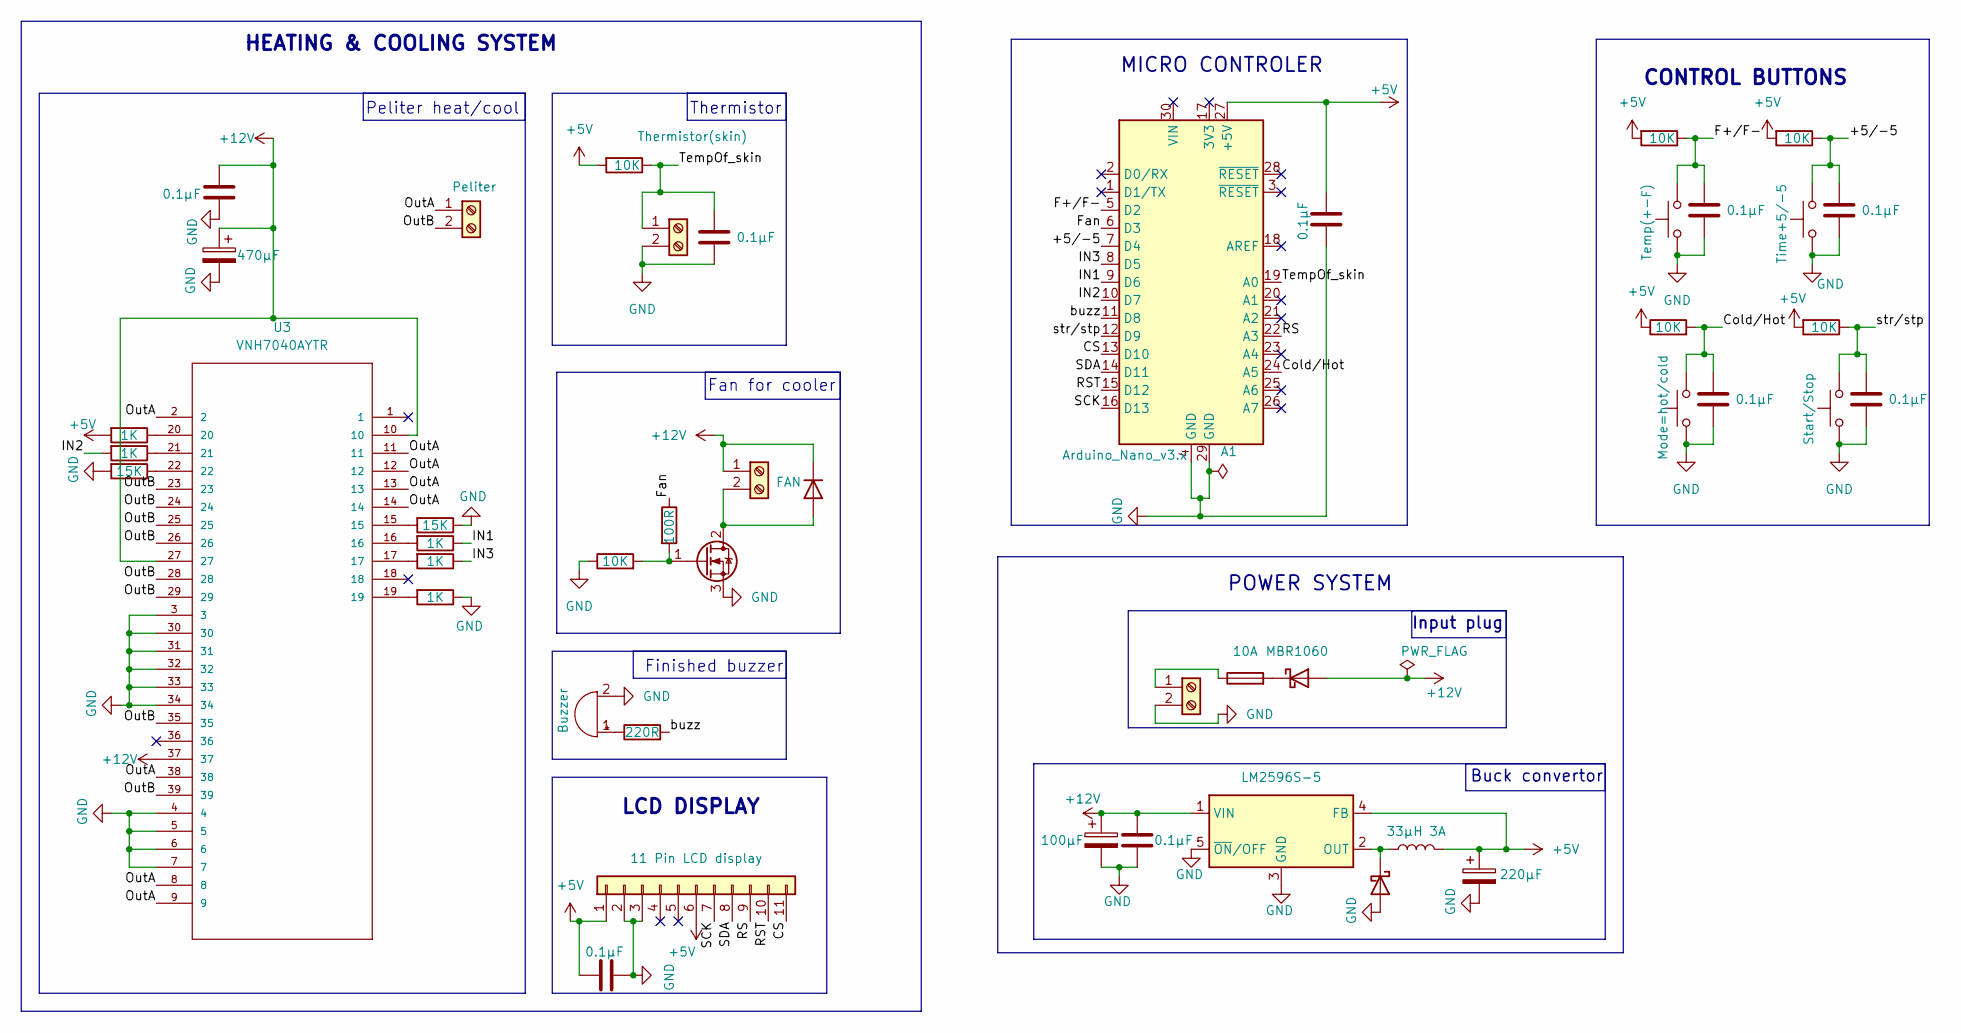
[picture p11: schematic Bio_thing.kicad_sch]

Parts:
A1: Arduino_Nano_v3.x; Untitled
BZ1: Buzzer; Buzzer_12x9.5RM7.6
C1, C3, C4, C5, C6, C9, C10, C11, C15: 0.1µF; C_0805_2012Metric
C2: 220µF; CP_Elec_6.3x7.7
C8: 100µF; C_1206_3216Metric
C16: 470µF; CP_Elec_8x10.5
D1: 1N4001; D_SMA_Handsoldering
D2: 1N5822; D_SMA_Handsoldering
D4: MBR1060; TO-220-2_Vertical
F2: 10A; Fuseholder_Cylinder-5x20mm_Schurter_0031_8201_Horizontal_Op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
Fan_for_cooler1: IRLB8721PBF; TO-220-3_Vertical
J1: FAN; TerminalBlock_Phoenix_PT-1,5-2-5.0-H_1x02_P5.00mm_Horizontal
J2: Peliter; TerminalBlock_Phoenix_PT-1,5-2-5.0-H_1x02_P5.00mm_Horizontal
J3: Screw_Terminal_01x02; TerminalBlock_Phoenix_PT-1,5-2-5.0-H_1x02_P5.00mm_Horizontal
J5: Thermistor(skin); TerminalBlock_Phoenix_PT-1,5-2-5.0-H_1x02_P5.00mm_Horizontal
J8: 11 Pin LCD display; PinSocket_1x11_P2.54mm_Vertical
L1: 33µH 3A; L_Radial_D8.7mm_P5.00mm_Fastron_07HCP
R1, R2, R3, R8, R9, R10: 10K; R_0805_2012Metric
R4, R5, R6, R7, R19: 1K; R_0805_2012Metric
R11: 100R; R_0805_2012Metric
R12, R14: 15K; R_0805_2012Metric
R13: 220R; R_0805_2012Metric
SW2: Mode=hot/cold; SW_PUSH_6mm_H4.3mm
SW3: Start/Stop; SW_PUSH_6mm_H4.3mm
SW4: Temp(+-F); SW_PUSH_6mm_H4.3mm
SW5: Time+5/-5; SW_PUSH_6mm_H4.3mm
U1: LM2596S-5; TO-263-5_TabPin3
U3: VNH7040AYTR; POWERSSO-36TP_STM; MANUFACTURER_PART_NUMBER VNH7040AYTR

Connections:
+5V: A1.27 (+5V), C2.1, C10.1, C11.2, J8.1, J8.6, L1.2, R2.2, R3.2, R8.2, R9.2, R10.1, R19.2, U1.4 (FB)
+12V: C8.1, C9.1, C15.1, C16.1, D1.1 (K), D4.2 (A), J1.1, U1.1 (VIN), U3.10, U3.27, U3.37
/+5/-5: A1.7 (D4), C6.1, R9.1, SW5.2
/CS: A1.13 (D10), J8.11
/Cold/Hot: A1.24 (A5), C5.1, R10.2, SW2.2
/F+/F-: A1.5 (D2), C3.1, R8.1, SW4.2
/Fan: A1.6 (D3), R11.1
/IN1: A1.9 (D6), R4.1
/IN2: A1.10 (D7), R5.2
/IN3: A1.8 (D5), R6.1
/OutA: J2.1, U3.2, U3.8, U3.9, U3.11, U3.12, U3.13, U3.14, U3.38
/OutB: J2.2, U3.23, U3.24, U3.25, U3.26, U3.28, U3.29, U3.35, U3.39
/RS: A1.22 (A3), J8.9
/RST: A1.15 (D12), J8.10
/SCK: A1.16 (D13), J8.7
/SDA: A1.14 (D11), J8.8
/TempOf_skin: A1.19 (A0), C4.1, J5.1, R2.1
/buzz: A1.11 (D8), R13.2
/str/stp: A1.12 (D9), C1.1, R3.1, SW3.2
GND: A1.4 (GND), A1.29 (GND), BZ1.2 (-), C1.2, C2.2, C3.2, C4.2, C5.2, C6.2, C8.2, C9.2, C10.2, C11.1, C15.2, C16.2, D2.2 (A), Fan_for_cooler1.3 (S), J3.2, J5.2, J8.2, J8.3, R1.1, R7.1, R12.1, R14.2, SW2.1, SW3.1, SW4.1, SW5.1, U1.3 (GND), U1.5 (~ON/OFF), U3.3, U3.4, U3.5, U3.6, U3.7, U3.30, U3.31, U3.32, U3.33, U3.34
unnamed: BZ1.1 (+), R13.1
unnamed: D1.2 (A), Fan_for_cooler1.2 (D), J1.2
unnamed: D2.1 (K), L1.1, U1.2 (OUT)
unnamed: D4.1 (K), F2.2
unnamed: Fan_for_cooler1.1 (G), R1.2, R11.2
unnamed: F2.1, J3.1
unnamed: R4.2, U3.16
unnamed: R5.1, U3.21
unnamed: R6.2, U3.17
unnamed: R7.2, U3.19
unnamed: R12.2, U3.15
unnamed: R14.1, U3.22
unnamed: R19.1, U3.20

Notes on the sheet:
Thermistor
MICRO CONTROLER
Peliter heat/cool
POWER SYSTEM
HEATING & COOLING SYSTEM
LCD DISPLAY
Buck convertor
Finished buzzer
Input plug
Fan for cooler
CONTROL BUTTONS

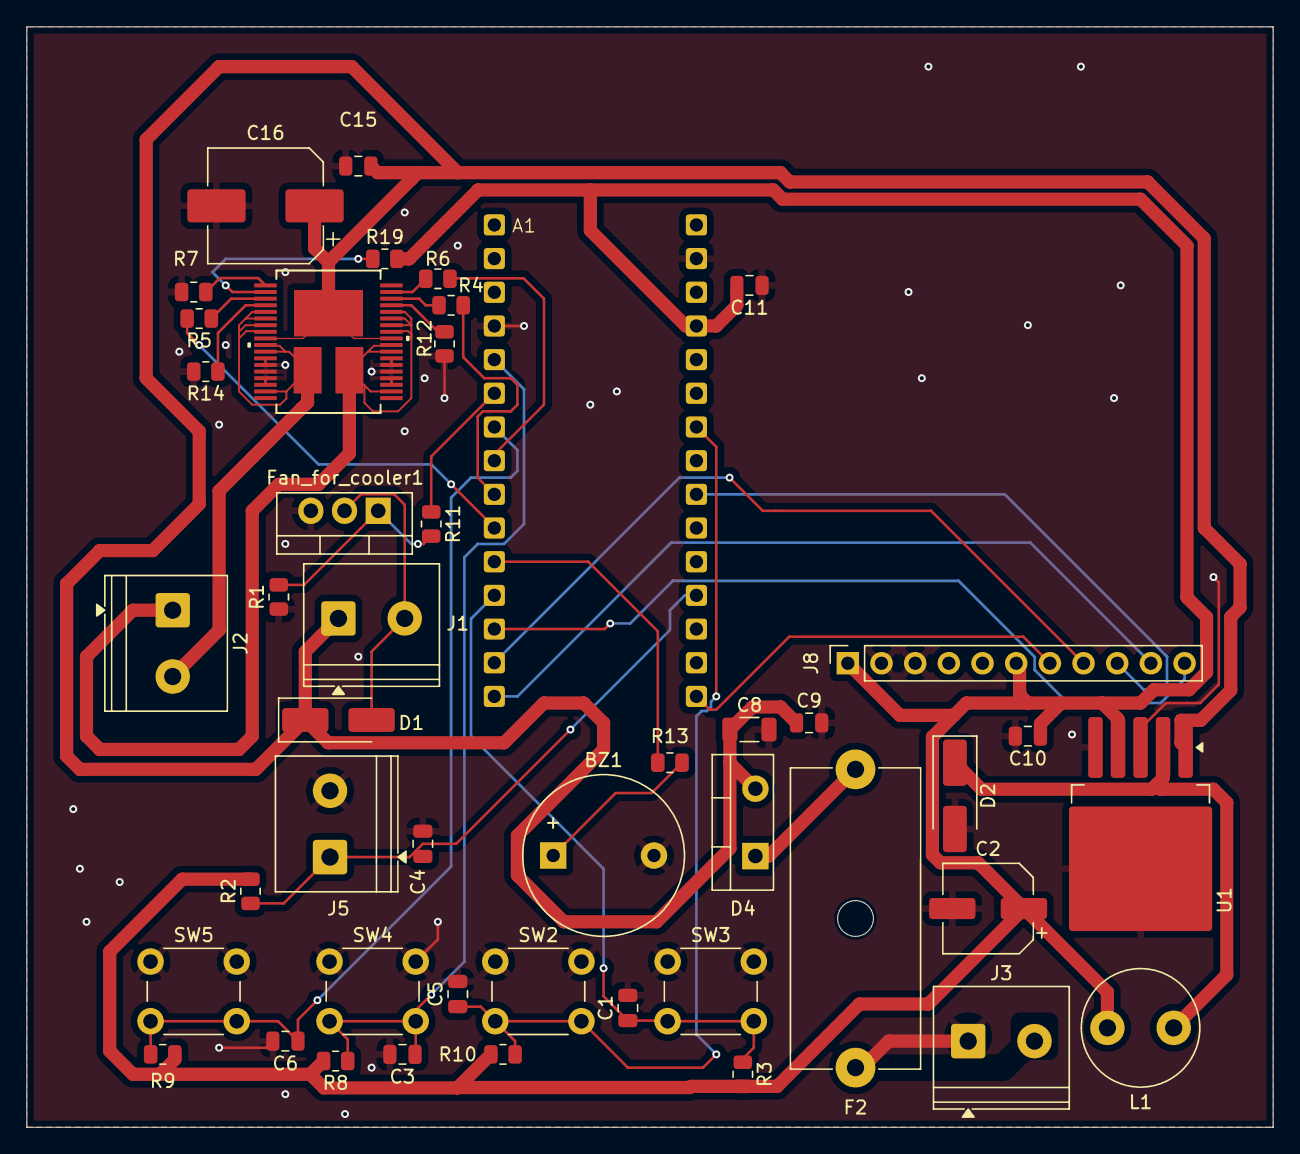
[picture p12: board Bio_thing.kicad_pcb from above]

Board: 2 copper layers, 94.0 x 83.0 mm, 46 parts (0 on the bottom side), 33 nets.

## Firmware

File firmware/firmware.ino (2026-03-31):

//Ardunio TheraPatch Firmware :p :p



#include <Adafruit_GFX.h>     
#include <Adafruit_ST7735.h>    
#include <SPI.h>               


Adafruit_ST7735 tft(10, A3, 12);  

// Arduino pin map
#define BTN_TEMP  2     
#define BTN_TIME  4     
#define BTN_MODE  A5    
#define BTN_START 9     
#define PIN_INA   6     
#define PIN_INB   7     
#define PIN_PWM   5     
#define PIN_FAN   3     
#define PIN_THERM A0   
#define PIN_BUZZ  8     

// constraints/saftey setting
#define TEMP_MIN    35      // min temp
#define TEMP_MAX    120     // max temp
#define OVERHEAT_F  125     // shutoff if it reaches this max
#define DEFAULT_T   60      // defualt temp
#define DEFAULT_S   300     // default time
#define COLD_F      59      // cool mode auto set
#define HOT_F       105     // hot mode auto set
#define PWM_POWER   200      
#define HOLD_MS     2000    
#define BUZZ_MS     5000    

// LCD COLOR
#define C_HOT   0xFB20   // orange-red
#define C_COLD  0x5DFF   // light blue
#define C_GREEN 0x07E0
#define C_GREY  0x8410

// GLOBAL STATE
int setTemp = DEFAULT_T, setTime = DEFAULT_S;
bool isCold = false, running = false;
bool tempNeg = false, timeNeg = false;       
bool buzzing = false, forceRedraw = true;
unsigned long lastTick = 0, buzzStart = 0;
// display cache (avoids redrawing unchanged values)
int pT = -1, pS = -1; bool pC = false, pR = false; float pH = -999;

//BUTTON BIG
struct Btn {
  uint8_t pin;
  bool last;
  bool held;
  unsigned long downAt;
  unsigned long dbAt;
};

Btn btnT = {2,   1, 0, 0, 0};  // temp button: D2
Btn btnS = {4,   1, 0, 0, 0};  // time button:D4
Btn btnM = {A5,  1, 0, 0, 0};  // mode button: A5
Btn btnX = {9,   1, 0, 0, 0};  // str/stp: D9

uint8_t readBtn(Btn &b) {

  bool raw = digitalRead(b.pin);

  uint8_t ev = 0;

  // noise filter
  bool changed = (raw != b.last);
  bool stable  = (millis() - b.dbAt > 50);

  if (changed && stable) {
    b.dbAt = millis();
    b.last = raw;

    if (raw == LOW) {
      b.held = false;           // new press
      b.downAt = millis();      
    }
    else {
      if (!b.held) ev = 1;      // short press
    }
  }

  bool down    = (b.last == LOW);
  bool fresh   = (!b.held);
  bool twoSec  = (millis() - b.downAt >= HOLD_MS);

  if (down && fresh && twoSec) {
    b.held = true;              
    ev = 2;                     // hold for 2+ Sec, flips temp from + to - or vise versa
  }

  // 0 = nothing
  // 1 = short press
  // 2 = hold
  return ev;
}

//THERMISTOR TO READ TEMP

float readThermF() {
  int raw = max(analogRead(PIN_THERM), 1);
  float resistance = 10000.0 / (1023.0 / raw - 1.0);
  float kelvin = log(resistance / 10000.0) / 3950.0 + 1.0 / 298.15;

  float celsius    = (1.0 / kelvin) - 273.15;
  float fahrenheit = celsius * 9.0 / 5.0 + 32.0; //convesrion cuz i dont like celsius 

  return fahrenheit;
}

// PELTIER + FAN CONTROL

void peltierOff() {
  digitalWrite(PIN_INA, LOW);
  digitalWrite(PIN_INB, LOW);
  analogWrite(PIN_PWM, 0);
  digitalWrite(PIN_FAN, LOW);
}

// peltier on
void peltierOn() {
  // Cold: INA on but INB off 
  // Hot:  INA off but INB on
  if (isCold) {
    digitalWrite(PIN_INA, HIGH);
    digitalWrite(PIN_INB, LOW);
  } else {
    digitalWrite(PIN_INA, LOW);
    digitalWrite(PIN_INB, HIGH);
  }

  analogWrite(PIN_PWM, PWM_POWER);  
  digitalWrite(PIN_FAN, HIGH);       
}

// REST TO FACTORY SETTINGS
void resetAll() {
  running = false;
  setTemp = DEFAULT_T;       
  setTime = DEFAULT_S;       
  isCold = false;          
  tempNeg = false;       
  timeNeg = false;           
  peltierOff();              
  forceRedraw = true;        
}
//Runs in 3 senarios 1: stop is pressed 2: Overheating 3:timer runs out


// LCD DRAWING CODE

void drawStatic() {
  tft.fillScreen(ST77XX_BLACK);

  // two grey divider lines
  tft.drawFastHLine(0, 36, tft.width(), C_GREY);
  tft.drawFastHLine(0, tft.height() - 30, tft.width(), C_GREY);

  // grey labels
  tft.setTextSize(1);
  tft.setTextColor(C_GREY);
  tft.setCursor(2, 2);
  tft.print("SET TEMP");
  tft.setCursor(tft.width() - 36, 2);
  tft.print("TIME");
  tft.setCursor(2, tft.height() - 12);
  tft.print("SENSOR:");
}

// lcd temp in top left
void drawTemp() {
  // erase old number
  tft.fillRect(0, 12, 75, 22, ST77XX_BLACK);

  // draw new number in white
  tft.setTextSize(2);
  tft.setTextColor(ST77XX_WHITE);
  tft.setCursor(2, 14);
  tft.print(setTemp);
  tft.setTextSize(1);
  tft.print("F");

  // draw +/- indicator green:+ red:-
  tft.fillRect(62, 2, 10, 10, ST77XX_BLACK);
  tft.setCursor(62, 2);
  if (tempNeg) {
    tft.setTextColor(C_HOT);
    tft.print("-");
  } else {
    tft.setTextColor(C_GREEN);
    tft.print("+");
  }
}

// lcd timer
void drawTime() {
  char buf[6];
  sprintf(buf, "%02d:%02d", setTime / 60, setTime % 60);
  // erase old time
  int x = tft.width() - 62;
  tft.fillRect(x, 12, 62, 22, ST77XX_BLACK);
  // draw new time in white
  tft.setTextSize(2);
  tft.setTextColor(ST77XX_WHITE);
  tft.setCursor(x, 14);
  tft.print(buf);
  // draw +/- indicator
  tft.fillRect(tft.width() - 46, 2, 10, 10, ST77XX_BLACK);
  tft.setTextSize(1);
  tft.setCursor(tft.width() - 46, 2);
  if (timeNeg) {
    tft.setTextColor(C_HOT);
    tft.print("-");
  } else {
    tft.setTextColor(C_GREEN);
    tft.print("+");
  }
}

// lcd mode (hot/cold)
void drawMode() {
  tft.fillRect(0, 42, tft.width(), 50, ST77XX_BLACK);

  // in the center draw hot or cold
  if (isCold) {
    tft.setTextSize(3);
    tft.setTextColor(C_COLD);
    tft.setCursor(tft.width() / 2 - 36, 48);
    tft.print("COLD");
  } else {
    tft.setTextSize(3);
    tft.setTextColor(C_HOT);
    tft.setCursor(tft.width() / 2 - 27, 48);
    tft.print("HOT");
  }

  // draw running or standby 
  if (running) {
    tft.setTextSize(1);
    tft.setTextColor(C_GREEN);
    tft.setCursor(tft.width() / 2 - 27, 78);
    tft.print("> RUNNING");
  } else {
    tft.setTextSize(1);
    tft.setTextColor(C_GREY);
    tft.setCursor(tft.width() / 2 - 27, 78);
    tft.print("  STANDBY");
  }
}

// lcd thermistor reading
void drawTherm(float f) {

  tft.fillRect(46, tft.height() - 14, 80, 12, ST77XX_BLACK);
  tft.setTextSize(1);
  tft.setTextColor(ST77XX_WHITE);
  tft.setCursor(46, tft.height() - 12);
  tft.print(f, 1);
  tft.print("F");
}

// lcd refresh loop
void refresh(float tf) {
  // redraw after reset
  if (forceRedraw) {
    drawStatic();
    drawTemp();
    drawTime();
    drawMode();
    drawTherm(tf);
    forceRedraw = false;
    pT = setTemp;
    pS = setTime;
    pC = isCold;
    pR = running;
    pH = tf;
    return;
  }

  // redraw what changed 
  if (setTemp != pT) { drawTemp(); pT = setTemp; }
  if (setTime != pS) { drawTime(); pS = setTime; }
  if (isCold != pC || running != pR) { drawMode(); pC = isCold; pR = running; }
  if (abs(tf - pH) > 0.3) { drawTherm(tf); pH = tf; }
}

// STARTUP WHEN ARDUINO POWER ON
void setup() {

  // button power
  pinMode(BTN_TEMP, INPUT_PULLUP);   
  pinMode(BTN_TIME, INPUT_PULLUP);  
  pinMode(BTN_MODE, INPUT_PULLUP);   
  pinMode(BTN_START, INPUT_PULLUP);  

  // peliter power
  pinMode(PIN_INA, OUTPUT);    
  pinMode(PIN_INB, OUTPUT);    
  pinMode(PIN_PWM, OUTPUT);  
  pinMode(PIN_FAN, OUTPUT);   
  pinMode(PIN_BUZZ, OUTPUT);  

 
  peltierOff();
  digitalWrite(PIN_BUZZ, LOW);

  // lcd wake up
  tft.initR(INITR_144GREENTAB);   
  tft.setRotation(1);              
  forceRedraw = true;
}

// MAIN LOOP THAT IS THE BEATING HEART OF THIS CODE
void loop() {

  //button check
  uint8_t eT = readBtn(btnT);   
  uint8_t eS = readBtn(btnS);
  uint8_t eM = readBtn(btnM);
  uint8_t eX = readBtn(btnX);

  // temp button long press
  if (eT == 2) {
    tempNeg = !tempNeg;
  }
  // temp button short press
  if (eT == 1) {
    if (tempNeg) {
      setTemp = setTemp - 1;    
    } else {
      setTemp = setTemp + 1;    
    }
    // keep temp within safe limits
    setTemp = constrain(setTemp, TEMP_MIN, TEMP_MAX);
  }

  // time button long press
  if (eS == 2) {
    timeNeg = !timeNeg;
  }
  // time button short press
  if (eS == 1) {
    if (timeNeg) {
      setTime = setTime - 5;
    } else {
      setTime = setTime + 5;
    }
    // don't let time go below 0
    if (setTime < 0) {
      setTime = 0;
    }
  }

 
  // mode button to switch between hot and cold
  if (eM == 1 && !running) {
    isCold = !isCold;          

    if (isCold) {
      setTemp = COLD_F;        
    } else {
      setTemp = HOT_F;         
    }
    tempNeg = false;           
  }

  // start stop
  if (eX == 1) {
    if (!running && setTime > 0) {
      // start
      running = true;
      lastTick = millis();     
      peltierOn();             
    }
    else if (running) {
      // stop which restets
      resetAll();
    }
  }

  // countdown
  if (running && millis() - lastTick >= 1000) {
    lastTick = lastTick + 1000;
    setTime = setTime - 1;

    if (setTime <= 0) {
      setTime = 0;
      running = false;
      peltierOff();          

      // start buzzer
      buzzing = true;
      buzzStart = millis();
      digitalWrite(PIN_BUZZ, HIGH);

      // reset all settings to defaults
      setTemp = DEFAULT_T;
      setTime = DEFAULT_S;
      isCold = false;
      tempNeg = false;
      timeNeg = false;
      forceRedraw = true;       
    }
  }
  // stop buzzer after 5 seconds
  if (buzzing && millis() - buzzStart >= BUZZ_MS) {
    digitalWrite(PIN_BUZZ, LOW);
    buzzing = false;
  }

  // themistor reader
  float tf = readThermF();

  //safety first
  if (running && tf > OVERHEAT_F) {
    peltierOff();
    running = false;

    // start buzzer
    buzzing = true;
    buzzStart = millis();
    digitalWrite(PIN_BUZZ, HIGH);

    // flash warning on screen
    tft.fillScreen(C_HOT);
    tft.setTextSize(2);
    tft.setTextColor(ST77XX_WHITE);
    tft.setCursor(10, 50);
    tft.print("OVERHEAT!");
    delay(3000);

    resetAll();
  }

  // screen update
  refresh(tf);
  delay(10);
}

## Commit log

2026-04-01 Update and rename BOM - Sheet1.csv to Bom/BOM - Sheet1.csv
    [BOM - Sheet1.csv]
2026-04-01 Rename Bom for JCLPCB - Sheet1 (1).csv to Bom/Bom for JCLPCB - Sheet1 (1).csv
    [Bom for JCLPCB - Sheet1 (1).csv]
2026-04-02 Rename CAD/Images/CASE.png to CAD /CASE.png

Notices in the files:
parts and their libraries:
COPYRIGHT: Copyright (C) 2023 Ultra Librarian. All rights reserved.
